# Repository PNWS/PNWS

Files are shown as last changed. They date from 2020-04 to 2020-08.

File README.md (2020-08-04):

## Do No Harm
Please ensure that if you are planning to deliver these to others that you sterilise them, always assume you are infected and take every precaution.

# PNWS
Face shield design to aid first line responders during the COVID19 Epidemic.   
This design was created by members of the Washington Sate 3D Face Shield Hub.  

If you are a medical professional and are in need of shields, please head to our website [faceshieldhub.org](https://www.faceshieldhub.org)

This is an update of "DtM-v3.1 Face Shield PPE, 3D printable headband NO LOGO", item 
3DPX-013359. 

# Available for Purchase
The PNWS is available for purchase at cost on amazon at the following link.  PLEASE MAKE SURE TO REMOVE THE PROTECTIVE FILM ON THE SHIELD BEFORE USE.
[https://www.amazon.com/dp/B08D7H37QX](https://www.amazon.com/dp/B08D7H37QX)

## Updates made based on clinical feedback are:
* Reduced mass and print time
* Improvements to shield retention while reducing stress applied to the shield itself.
* Thinned forehead section to reduce pressure on the forehead
* Mount peg spacing changed for equivalency to "Swedish" headband
* Added brimless variant to further reduce print time and mass
* Added engineering definition for face shield and headband
* Added cloth tie clips as an option
* Added option of foam headband
* Increased spacing to improve wearability with glasses and N95 mask underneath.
* Reduced weight solves for headaches from all-day wear of previous model

* Optimised build and assembly to standard materials that can be readily purchased (e.g., US letter-sized transparency)

## Product Point of View
Due to a domestic supply chain gap for transparent face shields, this remixed 3D printed design immediately provides personal protective equipment (PPE) to healthcare workers responding to COVID-19, and incorporates clinical feedback and clinical reviews from other similar designs being used across hospitals across the nation. Face shield characteristics: 
* limits aerosol and splatter exposure directly to the anterior head, specifically to the face and from above the head, while providing top ventilation to limit fogging and condensation
* reduces aerosol and splatter exposure on N95 and other face masks; this follows current recommendations to use full face shields to protect limited supply N95 masks
* re-usable for a single user (can survive multiple daily washes; transparent visor can be replaced from readily sourced materials when worn out)

easy to fabricate within a few days of design approval (i.e., no complex supply chains or production bottlenecks)
comfortable to wear and easy to don and doff (as it will be taken on and off dozens of times in a 12-24 hour shift)
provides protection to broader area of face compared to standard safety goggles or glasses

## LICENSING AND TERMS
License - Apache 2.

## Folder Structure
Once you download the fabrication package you will be see there is an assembly drawing and a BOM, please open these first to help decide which parts you would like to print.

## What to make?

### PNWS Frame:
Download the PNWS Full Release Package

NIH Link - https://3dprint.nih.gov/discover/3dpx-013883

### PNWS Short:
Download the PNWS Short Release Package

NIH Link - https://3dprint.nih.gov/discover/3dpx-013884

### Are any sliced files ready for my printer or ply cutter?

Yes! Please look at the [Sliced Files folder](https://github.com/mrjonny2/PNWS/tree/master/Sliced%20Files).  If you would like to contribute to these please reach out and we can get them added.

### What are the Cloth Ties?
If you can't get stretchy fabrics or button hole elastic use two cloth ties and any fabric or elastic to make a headband.

### How do I put it all together?
Please open: [PNWS Assembly Instructions.pdf](https://github.com/mrjonny2/PNWS/blob/master/PNWS%20Assembly%20Instructions.pdf)

## 3D PRINTING INFORMATION
__Please see the [Sliced Files folder](https://github.com/mrjonny2/PNWS/tree/master/Sliced%20Files) for files that are ready for cutting and printing__
### Printer technology/material
Intended Method - Fused Deposition Modeling

Acceptable Methods - Multi Jet Fusion, Selective Laser Sintering
### Printer Make/Model:
Intended: Testing and design carried out on Prusa Mk3 and Prusa Mk3S

Acceptable: Any printer using the technologies stated above
### Print Units:
mm (Detailed drawings for each part are provided)
### Scale at given print units:
1:1 scale
### Print Materials:
Preferred: PETG

Acceptable: ABS, PC, NYLON, PEEK, ULTEM, ASA or any other non-biodegradable polymer
### Number of prints per build build space:
Printer Dependant, 1 to multiple possible
### Print Time:
1h 3m using 0.6 nozzle, 0.4 layer height, pre-programmed settings.
### Pre- and post processing instructions:
Slicing required prior to printing specific to user's printer.   
#### Slice Recommendations for 0.4mm Nozzle
* Layer Height = 0.3mm
* First Layer height = 0.2mm
* Perimeters = 2
* Top solid layers = 3
* Bottom Solid Layers = 3
* Fill Density = 15%
* Fill pattern = Rectilinear
* No support Material
* No Raft    

This is generally identical to the Default PrusaSlicr 0.3mm Draft with the exception of reducing fill density to 15%.    

If you experience stringing on your prints, drop your nozzle temp for all but the first layer by 5C

Post-process as needed in accordance with provided drawings.

## Variants
There are a couple variations for this face shield, there is the shorty and the full variations which reduce mass while reducing the protection slightly.

The headband can also be swapped for the cloth tie clips and string or elasticated fabric

Shorty Variant:  
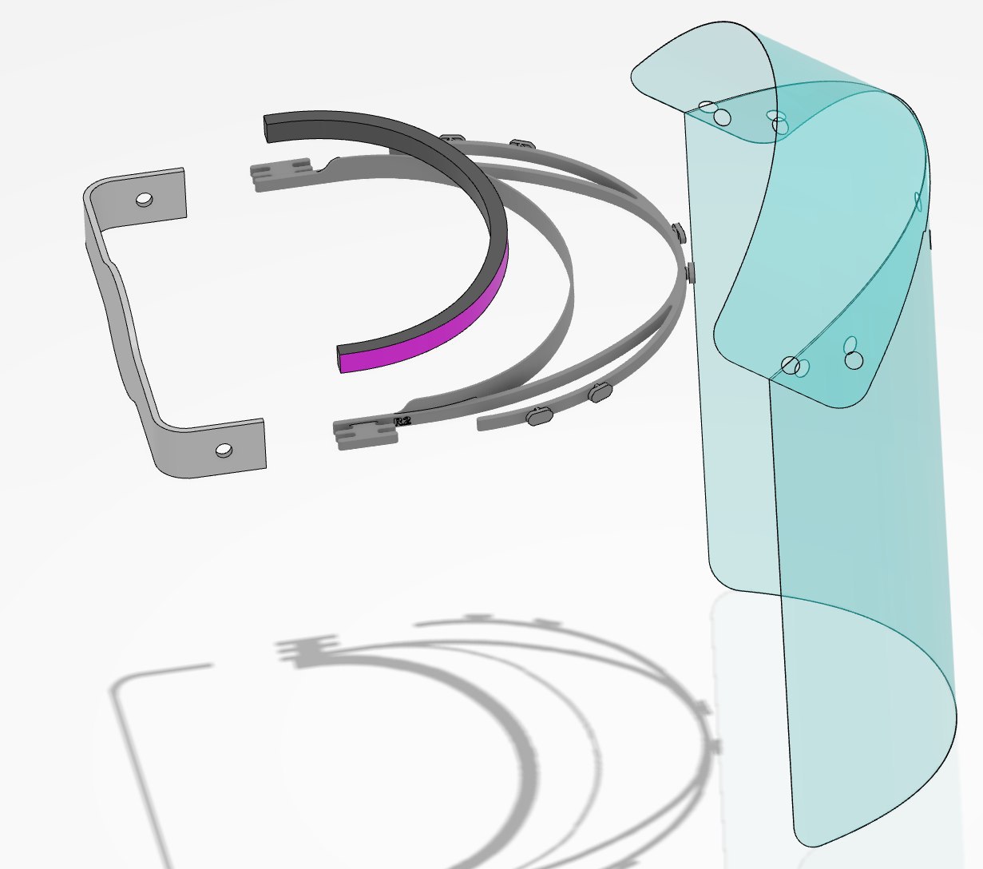
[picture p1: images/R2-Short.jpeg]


[Shorty]: https://raw.githubusercontent.com/mrjonny2/PNWS/master/images/R2-Short.jpeg "Shorty Variant"

Full Variant:  
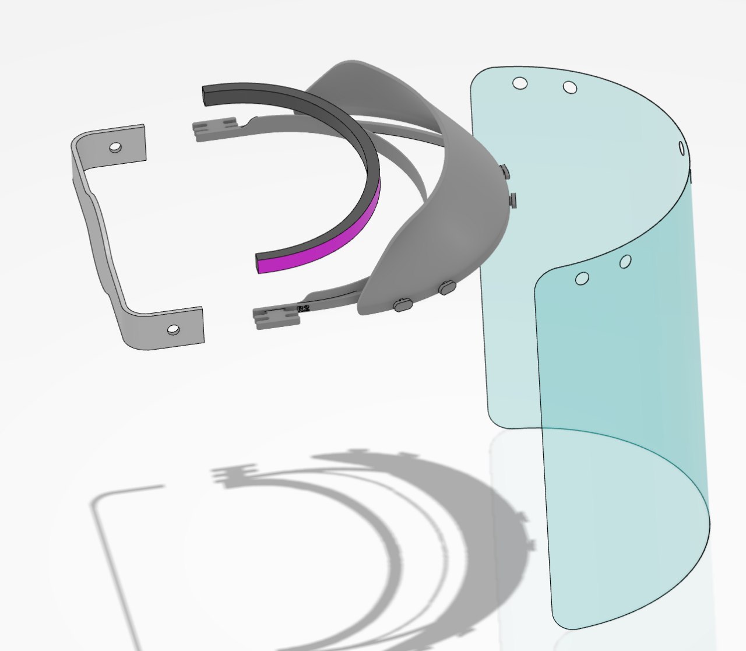
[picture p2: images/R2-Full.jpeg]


[Full]: https://raw.githubusercontent.com/mrjonny2/PNWS/master/images/R2-Full.jpeg "Full Variant"

## Shield Go-Gauge

If you are manufacturing shields, please print one of these go gauges to help verify that your hole punches are good.

## Contributors
Individuals directly contributing to this design include:

* Alice Ferng
* Inna Turevsky
* James Gwertzman
* Jason Vandervlugt
* Jonny Flowers
* Jon Friedman
* Mandi Mckay
* Neil Cueto
* Tom L
* Troy Hutt
* Yasuhiro Wabiko

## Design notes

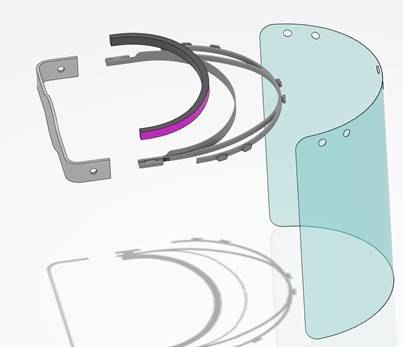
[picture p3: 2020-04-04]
images/R1-Short.jpg

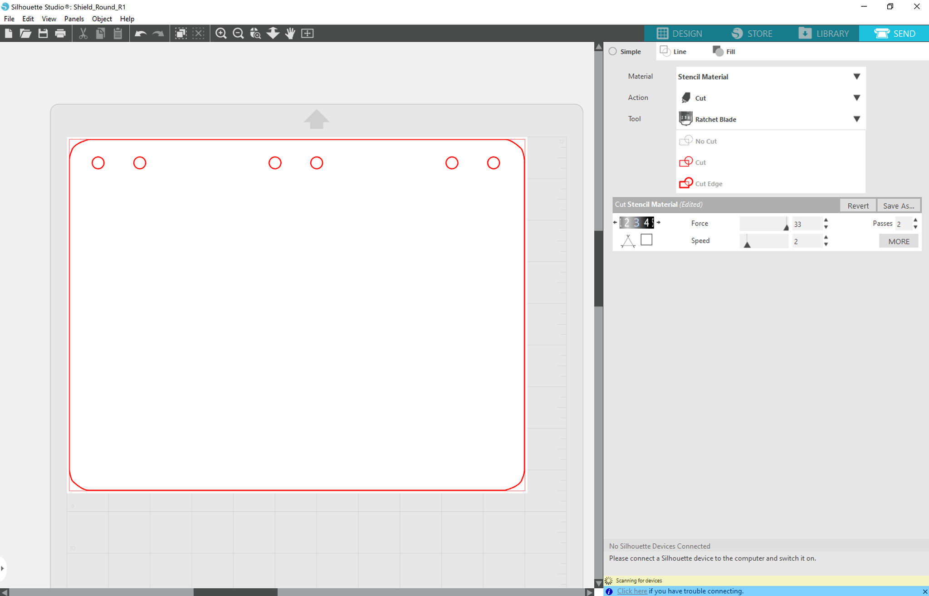
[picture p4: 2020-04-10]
Sliced Files/Silhouette Studio3/Studio3Screenshot.png

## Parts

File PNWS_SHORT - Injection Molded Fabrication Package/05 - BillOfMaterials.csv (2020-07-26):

Enovia Confidential Printed copies are Uncontrolled.
Generated on Jul 22
130879 rev 2: Engineering Bill of Materials
Level | Part Number | Revision | Specification Title | Qty | Type | Description
1 | 130879 | 2 | Asssmebly, Face Shield, PNWS | 1 | Assembly | Faceshield Released in response to the COVID19 epidemic released under MIT license
2 | 130007 | 3 | Headband Elastic | 1 | Part | Button hole elastic
2 | 128836 | 2 | Foam for Frame | 1 | Part | Neoprene Foam
2 | 130887 | 2 | Shield, Origami | 1 | Part | Polycarbonate shield
2 | 129016 | 2 | Frame, Short, PNWS, Injection Molding | 1 | Part | PET Injection molded frame

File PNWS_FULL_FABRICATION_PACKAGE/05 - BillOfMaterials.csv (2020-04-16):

Enovia Confidential Printed copies are Uncontrolled.
Generated on Apr 15
128827 rev 3: Engineering Bill of Materials
Level | Strap Variant | Revision | Specification Title | Qty | Type | Description
1 |  | 2 | ASSY, FACESHIELD, PNWS | 1 | Assembly | Faceshield Released in response to the COVID19 epidemic released under MIT license
2 | -- | 2 | FACESHIELD, FRAME, PNWS | 1 | Part
2 | -- | 1 | FACESHIELD, PNWS R1 | 1 | Part
2 | Headband | 1 | HEADBAND, FACESHIELD, PNWS | 1 | Part
2 | -- | 2 | FACESHIELD, FRAME, SHORT, PNWS | 1 | Part
2 | Cloth Tie | 1 | FACESHIELD, CLOTH TIE | 2 | Part | Optional for use with generic fabrics to tie mask
2 | -- | 1 | FACESHIELD, FOAM | 1 | Part

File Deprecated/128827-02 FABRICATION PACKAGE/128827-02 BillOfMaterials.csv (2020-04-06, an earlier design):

Enovia Confidential Printed copies are Uncontrolled.
Generated on Apr 6 |  |  | 2020 3:31:45 AM
128827 rev 2: Engineering Bill of Materials
Level | Shield Variant | Strap Variant | Part Number | Revision | Specification Title | Qty | Type | Description
1 |  |  | 128827 | 2 | ASSY, FACESHIELD, PNWS | 1 | Assembly | Faceshield Released in response to the COVID19 epidemic released under MIT license
2 | Brimmed | -- | 128828 | 2 | FACESHIELD, FRAME, PNWS | 1 | Part
2 | Brimmed | -- | 128829 | 1 | FACESHIELD, PNWS R1 | 1 | Part
2 | Both | Headband | 128830 | 1 | HEADBAND, FACESHIELD, PNWS | 1 | Part
2 | Short | -- | 128831 | 2 | FACESHIELD, FRAME, SHORT, PNWS | 1 | Part
2 | Both | Cloth Tie | 128835 | 1 | FACESHIELD, CLOTH TIE | 2 | Part | Optional for use with generic fabrics to tie mask
2 | Both | -- | 128836 | 1 | FACESHIELD, FOAM | 1 | Part
2 | Short | -- | 128839 | 1 | FACESHIELD, ORIGAMI, PNWS | 1 | Part

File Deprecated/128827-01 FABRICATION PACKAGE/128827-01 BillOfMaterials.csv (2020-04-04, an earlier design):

Enovia Confidential Printed copies are Uncontrolled.
Generated on Apr 4 |  |  | 2020 9:04:41 PM
128827 rev 1: Engineering Bill of Materials
Level | Shield Variant | Strap Variant | Part Number | Revision | Specification Title | State | Qty | Type | Description
1 |  |  | 128827 | 1 | ASSY, FACESHIELD, PNWS | Released | 1 | Assembly | Faceshield Released in response to the COVID19 epidemic released under MIT license
2 | Both | Both | 128829 | 1 | FACESHIELD, PNWS R1 | Released | 1 | Part
2 | Full | Both | 128828 | 1 | FACESHIELD, FRAME, PNWS | Released | 1 | Part
2 | Both | Band | 128830 | 1 | HEADBAND, FACESHIELD, PNWS | Released | 1 | Part
2 | Short | Both | 128831 | 1 | FACESHIELD, FRAME, SHORT, PNWS | Released | 1 | Part
2 | Both | Clothtie | 128835 | 1 | FACESHIELD, CLOTH TIE | Released | 2 | Part | Optional for use with generic fabrics to tie mask
2 | Both | Both | 128836 | 1 | FACESHIELD, FOAM | Released | 1 | Part

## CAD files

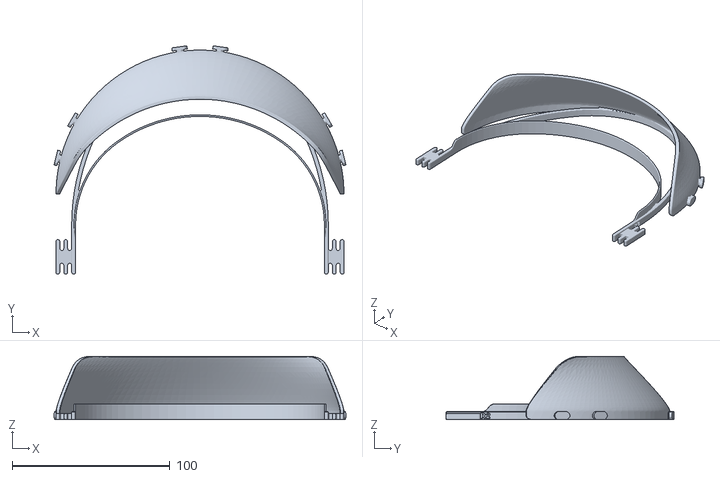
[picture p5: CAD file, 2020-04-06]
PNWS_FULL_FABRICATION_PACKAGE/06 - Frame - Full/06b - Frame - Full - STL.stl
185.0 x 144.7 x 40.0

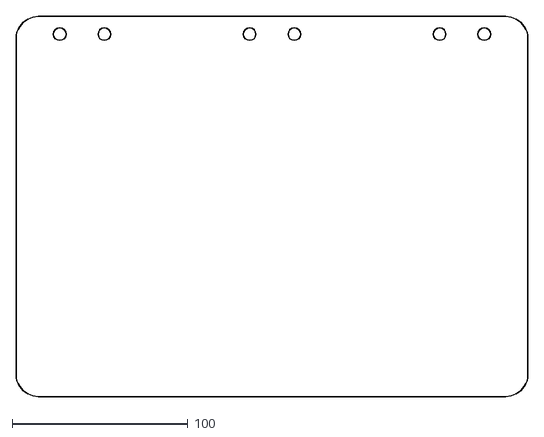
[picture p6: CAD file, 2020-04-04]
PNWS_FULL_FABRICATION_PACKAGE/07 - Shield/07c - Shield - DXF.dxf
290.9 x 216.0

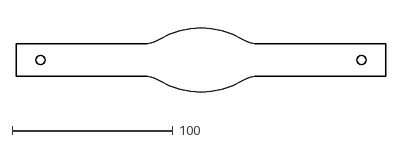
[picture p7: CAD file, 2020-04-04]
PNWS_FULL_FABRICATION_PACKAGE/08 - Headband - Elastic/08b - Headband - Elastic - DXF.dxf
229.8 x 44.8

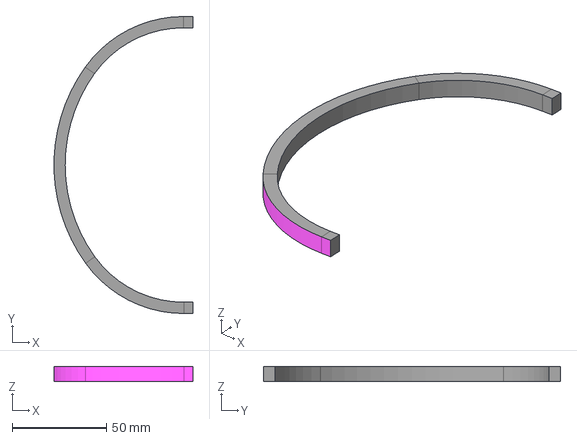
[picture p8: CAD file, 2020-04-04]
PNWS_FULL_FABRICATION_PACKAGE/09 - Foam - For Frame (Optional)/09c - Foam - For Frame - STP.stp
73.7 x 157.6 x 8.00 mm

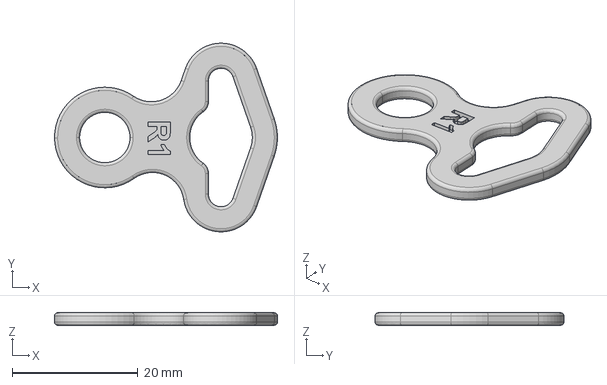
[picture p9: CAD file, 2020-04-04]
PNWS_FULL_FABRICATION_PACKAGE/10 - Cloth Tie (Optional)/10d - Cloth Tie - IGS.igs
35.4 x 30.0 x 2.00 mm

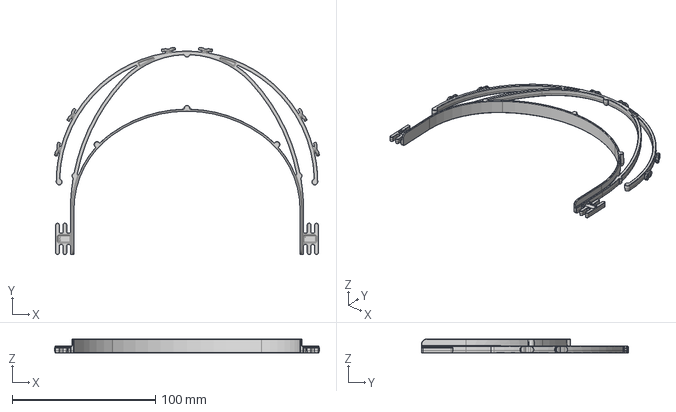
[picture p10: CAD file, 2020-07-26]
PNWS_SHORT - Injection Molded Fabrication Package/06 - Frame - Short - Injection Molding/06b - Frame - Short - Injection Molding - STEP.stp
184.8 x 144.6 x 10.0 mm

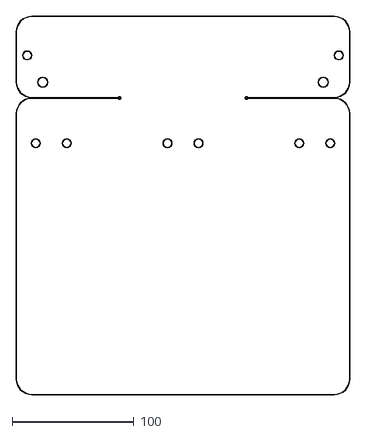
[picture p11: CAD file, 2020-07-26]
PNWS_SHORT - Injection Molded Fabrication Package/07 - Shield - Origami/07c - Shield - Origami - DXF.dxf
273.0 x 310.0

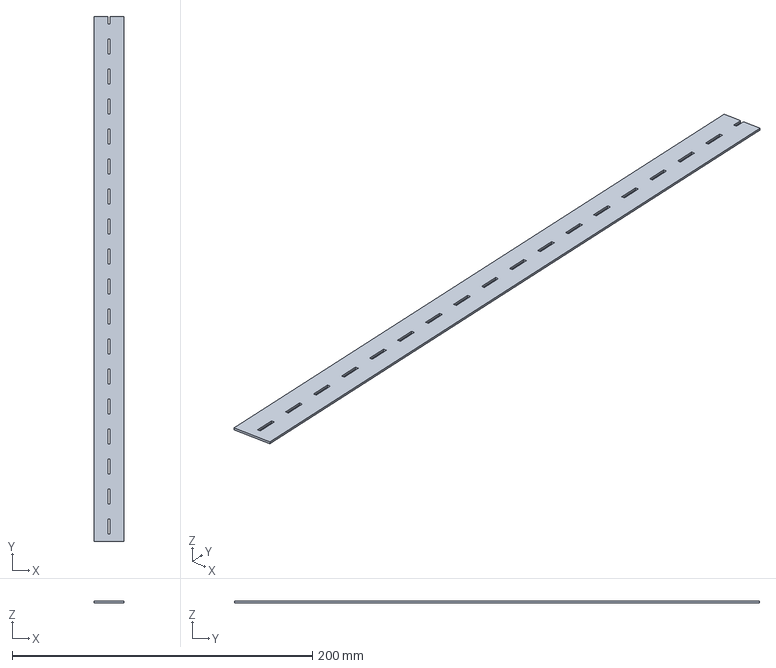
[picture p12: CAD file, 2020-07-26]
PNWS_SHORT - Injection Molded Fabrication Package/08 - Headband - Elastic/08c - Headband - Elastic - 3D IGS.igs
20.0 x 350.0 x 1.00 mm

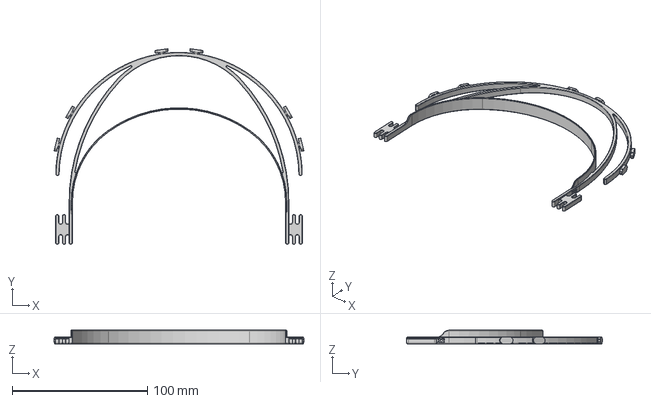
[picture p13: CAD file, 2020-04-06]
PNWS_SHORT_FABRICATION_PACKAGE/06 - Frame - Short/06d - Frame - Short - IGS.igs
185.0 x 144.7 x 10.0 mm

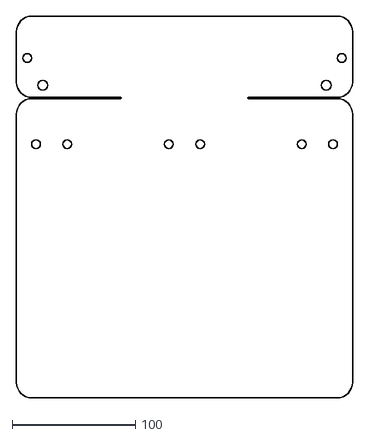
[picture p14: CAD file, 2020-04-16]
PNWS_SHORT_FABRICATION_PACKAGE/07 - Shield - Origami/07c - Shield - Origami - DXF.dxf
273.0 x 310.0

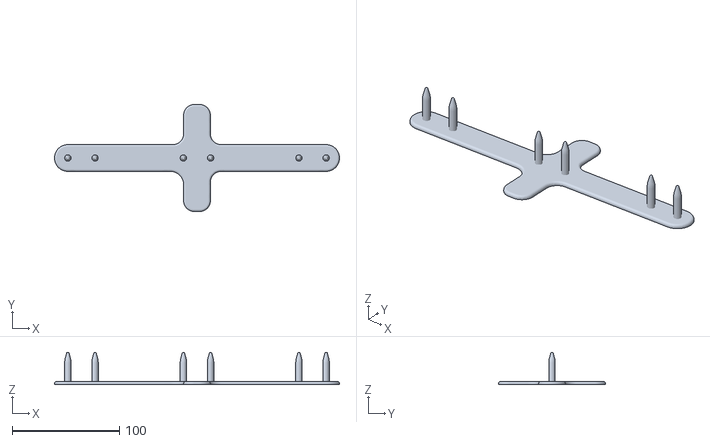
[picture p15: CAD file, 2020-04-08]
SHIELD GO GAUGE.stl
266.3 x 100.0 x 30.0

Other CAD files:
PNWS_FULL_FABRICATION_PACKAGE/06 - Frame - Full/06d - Frame - Full - IGS.igs
PNWS_FULL_FABRICATION_PACKAGE/06 - Frame - Full/06c - Frame - Full - STP.stp
PNWS_SHORT - Injection Molded Fabrication Package/09 - Foam - For Frame/09c - Foam for Frame - 3D IGS.igs
PNWS_SHORT_FABRICATION_PACKAGE/11 - Frame - Short - Injection Molding/11b - Frame - Short - Injection Molding - STP.stp
Deprecated/128827-01 FABRICATION PACKAGE/128828 FACESHIELD FRAME PNWS/128828-01 FACESHIELD FRAME PNWS A.1 Released.igs
Deprecated/128827-01 FABRICATION PACKAGE/128828 FACESHIELD FRAME PNWS/128828-01 FACESHIELD FRAME PNWS A.1 Released.stp
Deprecated/128827-01 FABRICATION PACKAGE/128829 FACESHIELD PNWS R1/128829-01 FACESHIELD PNWS R1 A.1 Released.igs
Deprecated/128827-01 FABRICATION PACKAGE/128829 FACESHIELD PNWS R1/128829-01 FACESHIELD PNWS R1 A.1 Released.stp
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

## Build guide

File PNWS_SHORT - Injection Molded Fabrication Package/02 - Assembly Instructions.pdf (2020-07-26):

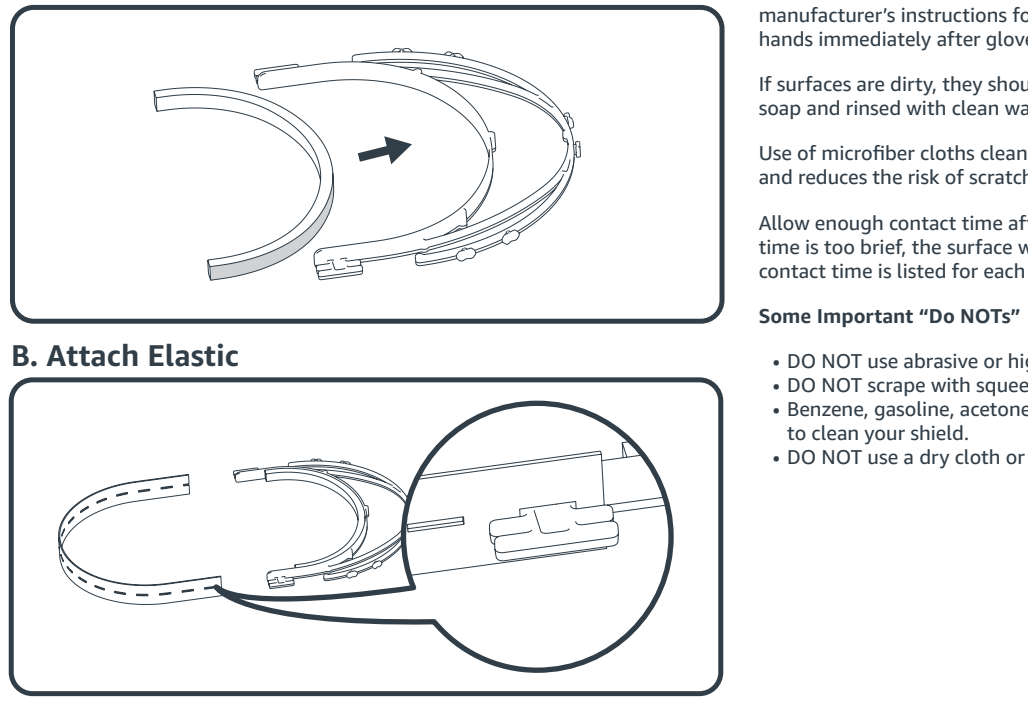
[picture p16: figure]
B. Attach Elastic; Some Important “Do NOTs”; to clean your shield.

## CLEANING METHODS

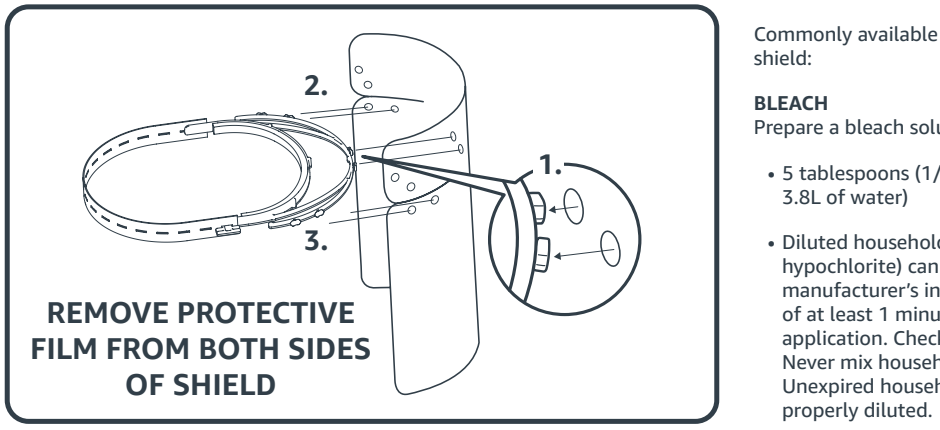
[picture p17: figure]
shield:; BLEACH; 3.8L of water); properly diluted.; REMOVE PROTECTIVE FILM FROM BOTH SIDES OF SHIELD

Commonly available disinfectants are recommended to be used on your face

Prepare a bleach solution by mixing:

- 5 tablespoons (1/3rd cup) bleach per gallon of water (80mL bleach per
- Diluted household bleach solutions (at least 1000ppm sodium hypochlorite) can be used if appropriate for the surface. Follow manufacturer’s instructions for application, ensuring a contact time of at least 1 minute, and allowing proper ventilation during and after application. Check to ensure the product is not past its expiration date. Never mix household bleach with ammonia or any other cleanser. Unexpired household bleach will be effective against coronaviruses when

SUPER SANI-WIPE, ISOPROPYL ALCOHOL [IPA] or ETHYL ALCOHOL
Use of alcohol-based wipes or sprays or soaked cloths containing at least 70%

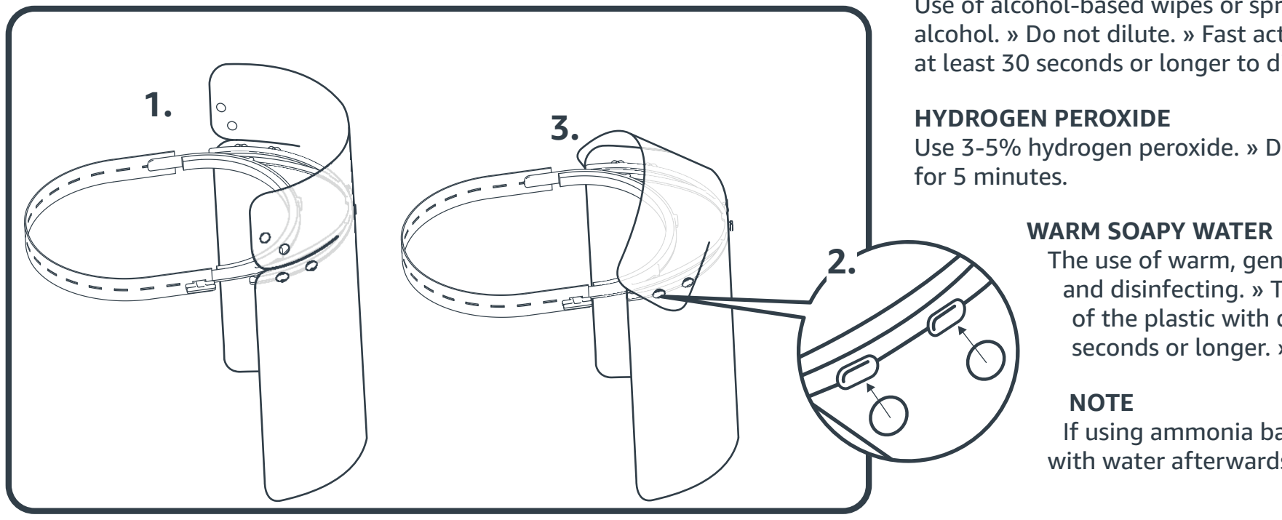
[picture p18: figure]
HYDROGEN PEROXIDE; for 5 minutes.; WARM SOAPY WATER; NOTE

alcohol. » Do not dilute. » Fast acting. Allow alcohol to remain on surface for at least 30 seconds or longer to disinfect.

Use 3-5% hydrogen peroxide. » Do not dilute. » Allow to remain on the plastic

The use of warm, gentle dish soap is a common form of cleaning and disinfecting. » Thoroughly and vigorously wash the surface of the plastic with dish washing soap for a minimum of 20 seconds or longer. » Rinse with clean water

If using ammonia based cleaners rinse down the clear shield with water afterwards to preserve optical clarity.

## A. Attach Foam

## C. Snap on Shield

## D. Fold Shield

## CLEANING INSTRUCTIONS

Wear disposable gloves when cleaning and disinfecting surfaces. Gloves should be discarded after each cleaning. If reusable gloves are used, those gloves should be dedicated for cleaning and disinfection of surfaces
for COVID-19 and should not be used for other purposes. Consult the manufacturer’s instructions for cleaning and disinfection products used. Clean hands immediately after gloves are removed.

If surfaces are dirty, they should be cleaned using a gentle warm dish washing soap and rinsed with clean water prior to disinfection.

Use of microfiber cloths cleans 50% better than comparable cotton towels and reduces the risk of scratching plastic.

Allow enough contact time after applying the disinfectant. If the contact time is too brief, the surface will not be thoroughly disinfected. Appropriate contact time is listed for each disinfectant listed below.

- DO NOT use abrasive or highly alkaline cleaners
- DO NOT scrape with squeegees, razor blades or other sharp instruments.
- Benzene, gasoline, acetone, or carbon tetrachloride should never be used
- DO NOT use a dry cloth or your hand to clean your polycarbonate!
Assembly Instructions - Open Source.indd 1 | 7/25/2020 10:09:41 PM

The Items are not intended for antimicrobial or antiviral protection or related uses, or uses for infection prevention or reduction or related uses, or for radiation protection, or any use that would create an undue risk in light of the public health emergency.

Copyright 2020 faceshieldhub.org

Licensed under the Apache License, Version 2.0 (the “License”); you may not use this file except in compliance with the License. You may obtain a copy of the License at:

http://www.apache.org/licenses/LICENSE-2.0

Unless required by applicable law or agreed to in writing, software distributed under the License is distributed on an “AS IS” BASIS, WITHOUT WARRANTIES OR CONDITIONS OF ANY KIND, either express or implied. See the License for the specific language governing permissions and limitations under the License.

These face shields are provided in parts meant to be assembled by the user.

The Items in this kit are not sterile.

Cleaning Methods are included with the Items in this package. Follow all cleaning agent manufacturer recommendations.

Assembly Instructions are included with the items in this package.

Alert: The design and materials for these face shields (“Items”) have been “Reviewed for Clinical Use” and made available by NIH/NIAD in collaboration with the U.S. Food and Drug Administration, the Veterans Healthcare Administration, and America Makes under on the NIH 3D Print Exchange (https://3dprint.nih.gov/collections/covid-19-response) including the following statements:

This design has undergone review in a clinical setting and has been found appropriate when fabricated with the printer type and materials specified.

https://3dprint.nih.gov/discover/3dpx-013884

March 25, 2020: [The NIH 3D Print Exchange] collection of designs was created to support the manufacturing of personal protective equipment (PPE) or other necessary medical devices that are in short supply due to the COVID-19 outbreak. While many can be printed with a 3D printer at home or your local Maker space, the NIH, FDA, VA, America Makes, and the contributing creators cannot ensure the quality, safety, and efficacy of these designs when manufactured without proper quality controls and processes.

We are proud to support you, and we thank you for all you are doing for our communities. We are grateful for your efforts.

NON
STERILE

This face shield was designed by an open source group of volunteers, source files and attributions can be found here:

github.com/PNWS/PNWS

For further information on products available for disinfecting your face shield, please visit:

https://www.epa.gov/pesticide-registration/list-n-disinfectants-use-against-sars-cov-2-covid-19

The Items contain materials which will contact the human body, including:

- Polyethylene Terephthalate Glycol (PETG) for the frame
- Polycarbonate (PC) for the shield
- Neoprene or Vinyl for the closed cell foam
- Cotton, Polyester, and Elastic for the headband, which may contain Latex

The Items are not intended for use in the presence of a high intensity heat sources or flammable gas. These Items should not be shared between users.

Document Version 2

Assembly Instructions - Open Source.indd 2 | 7/25/2020 10:09:41 PM

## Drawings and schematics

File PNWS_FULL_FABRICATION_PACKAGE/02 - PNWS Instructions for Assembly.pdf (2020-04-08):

# PNWS

# FACE SHIELD ASSEMBLY

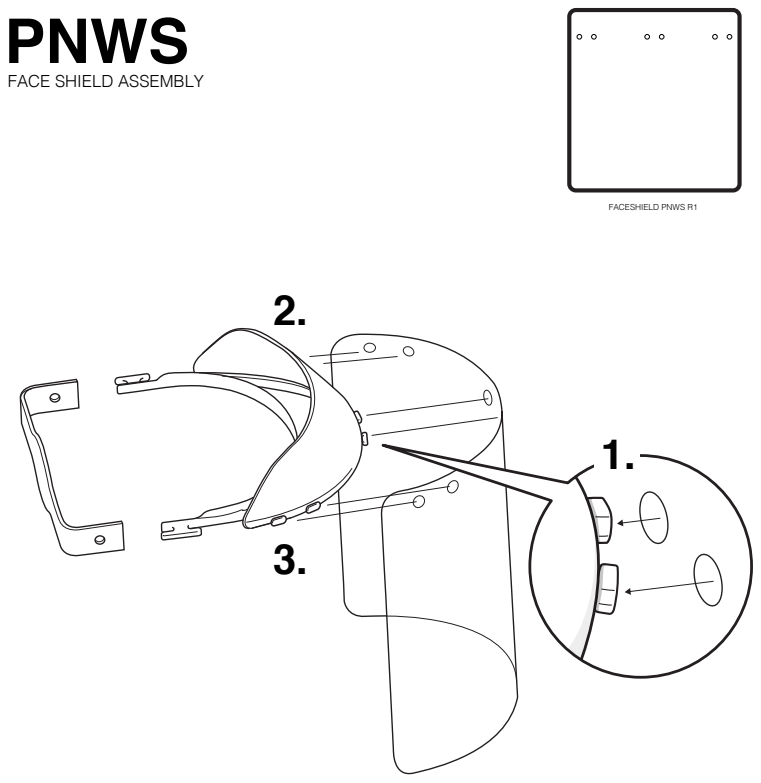
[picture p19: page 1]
FACESHIELD PNWS R1

# PNWS-SHORT

# FACE SHIELD ASSEMBLY

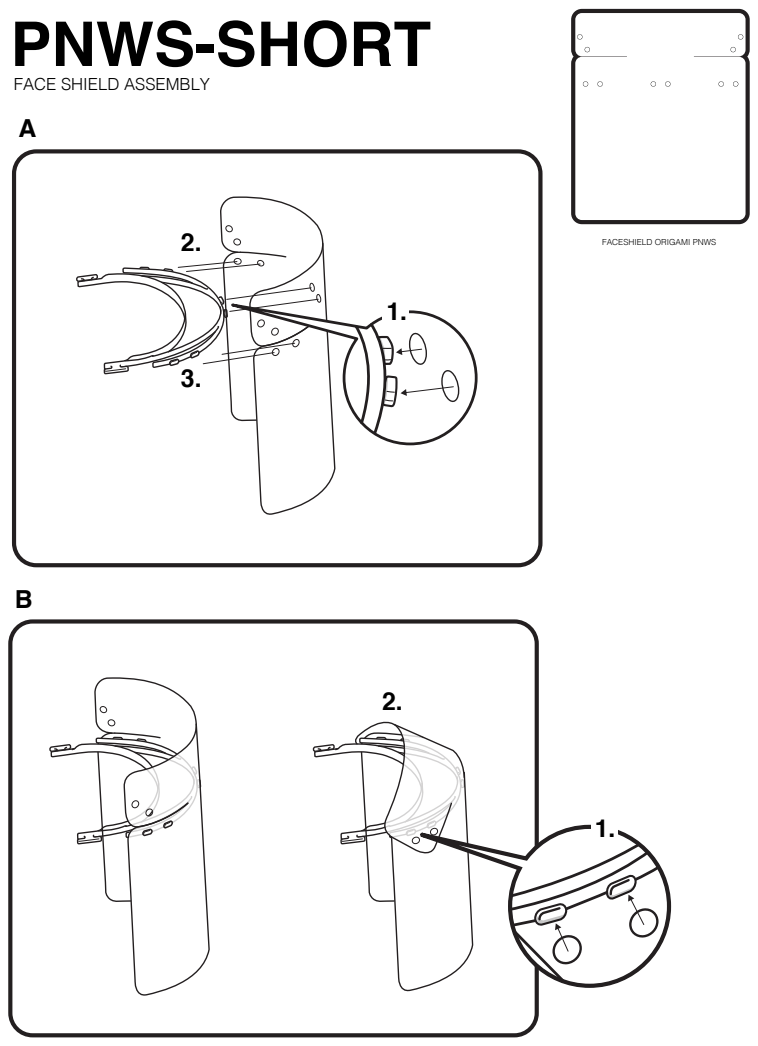
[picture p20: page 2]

2. FACESHIELD ORIGAMI PNWS

# PNWS

# HEADBAND ASSEMBLY

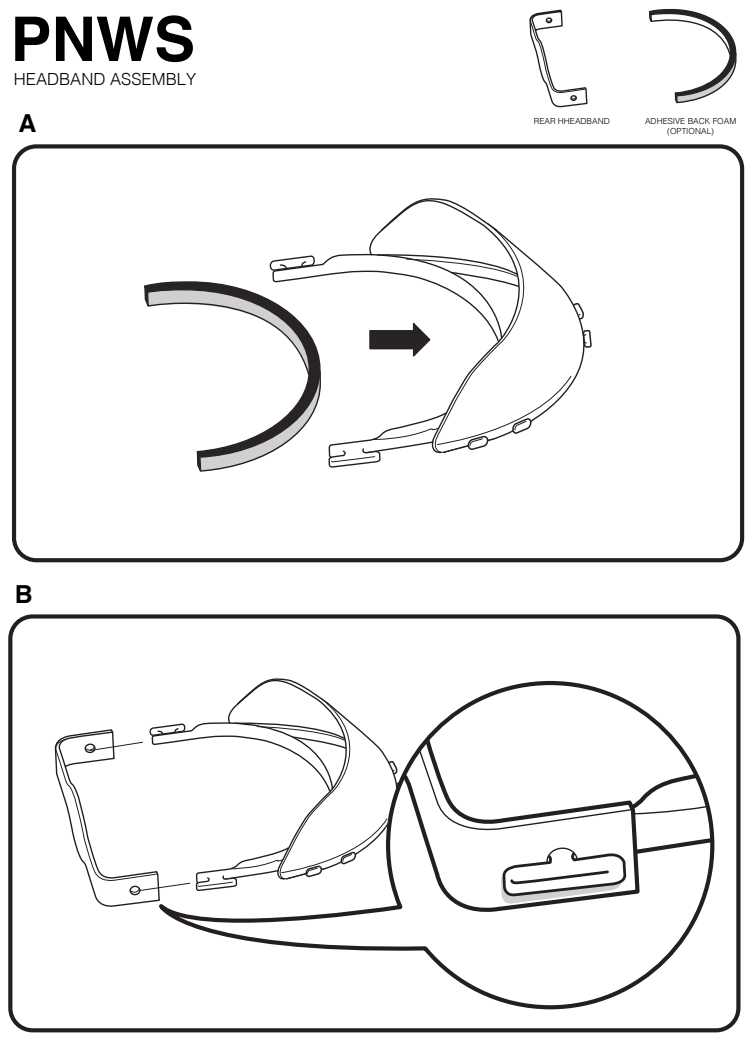
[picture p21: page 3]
(OPTIONAL) A; REAR HHEADBAND

ADHESIVE BACK FOAM

# PNWS

# HEADBAND ASSEMBLY

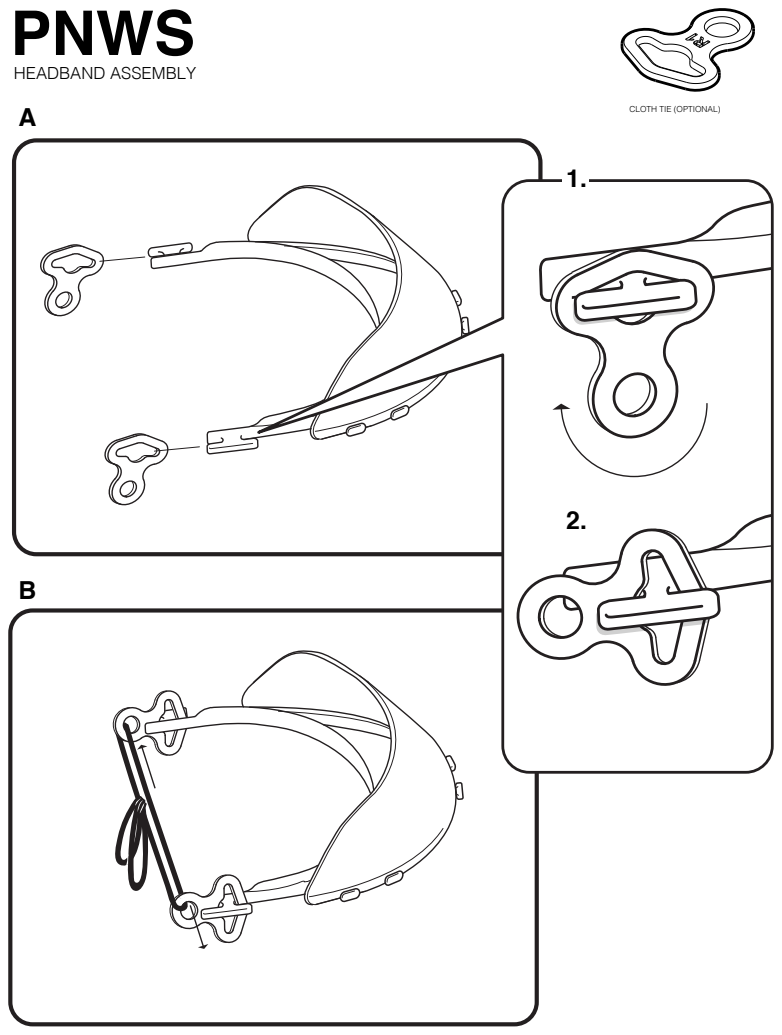
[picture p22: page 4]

CLOTH TIE (OPTIONAL) A

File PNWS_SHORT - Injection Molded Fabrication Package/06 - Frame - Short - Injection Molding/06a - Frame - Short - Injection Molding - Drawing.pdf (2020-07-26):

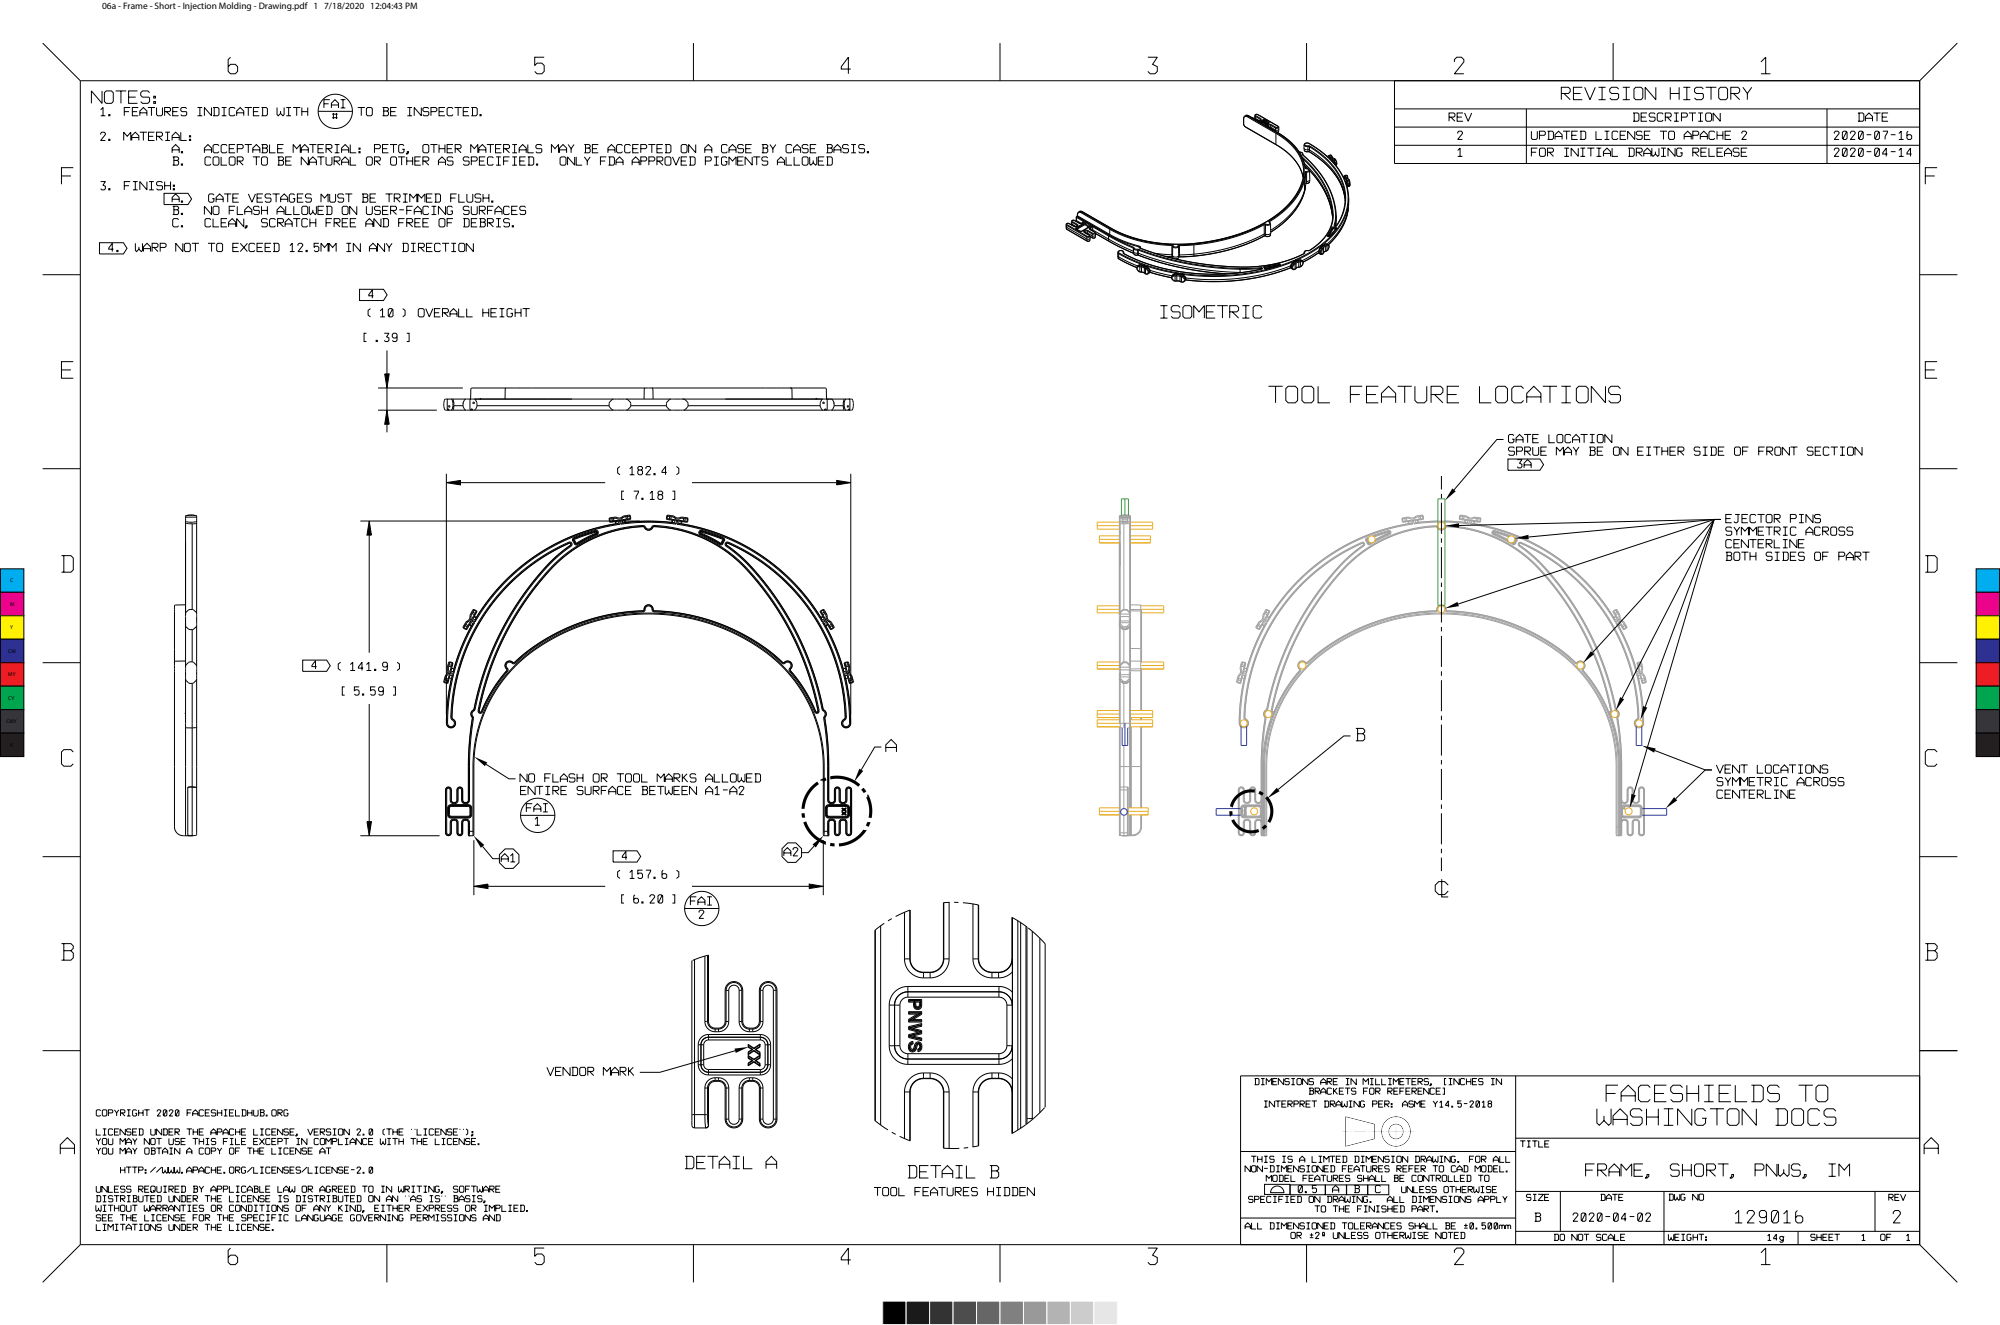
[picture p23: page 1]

06a - Frame - Short - Injection Molding - Drawing.pdf 1 7/18/2020 12:04:43 PM

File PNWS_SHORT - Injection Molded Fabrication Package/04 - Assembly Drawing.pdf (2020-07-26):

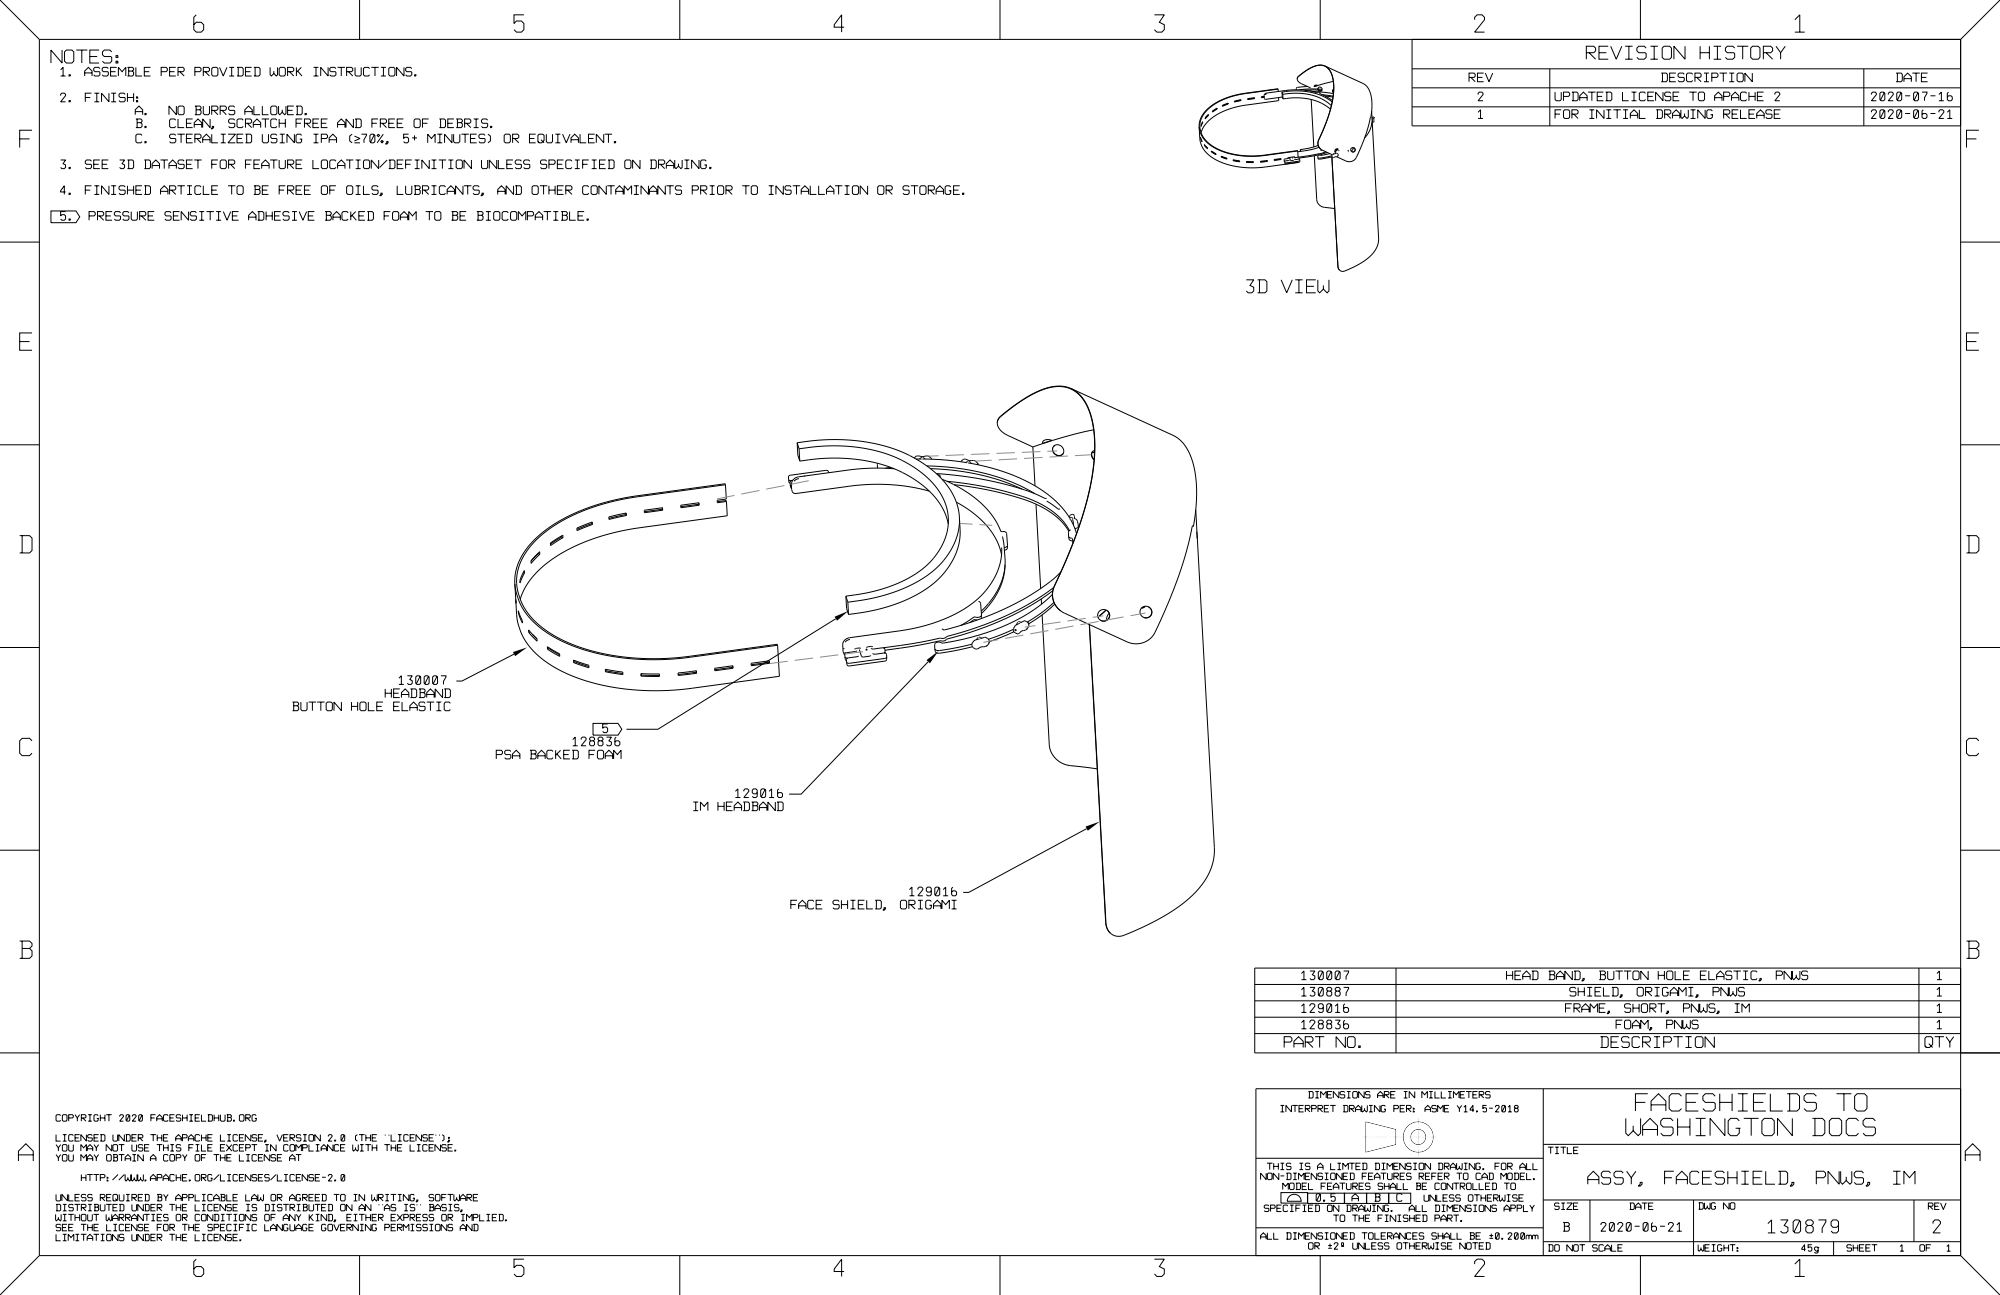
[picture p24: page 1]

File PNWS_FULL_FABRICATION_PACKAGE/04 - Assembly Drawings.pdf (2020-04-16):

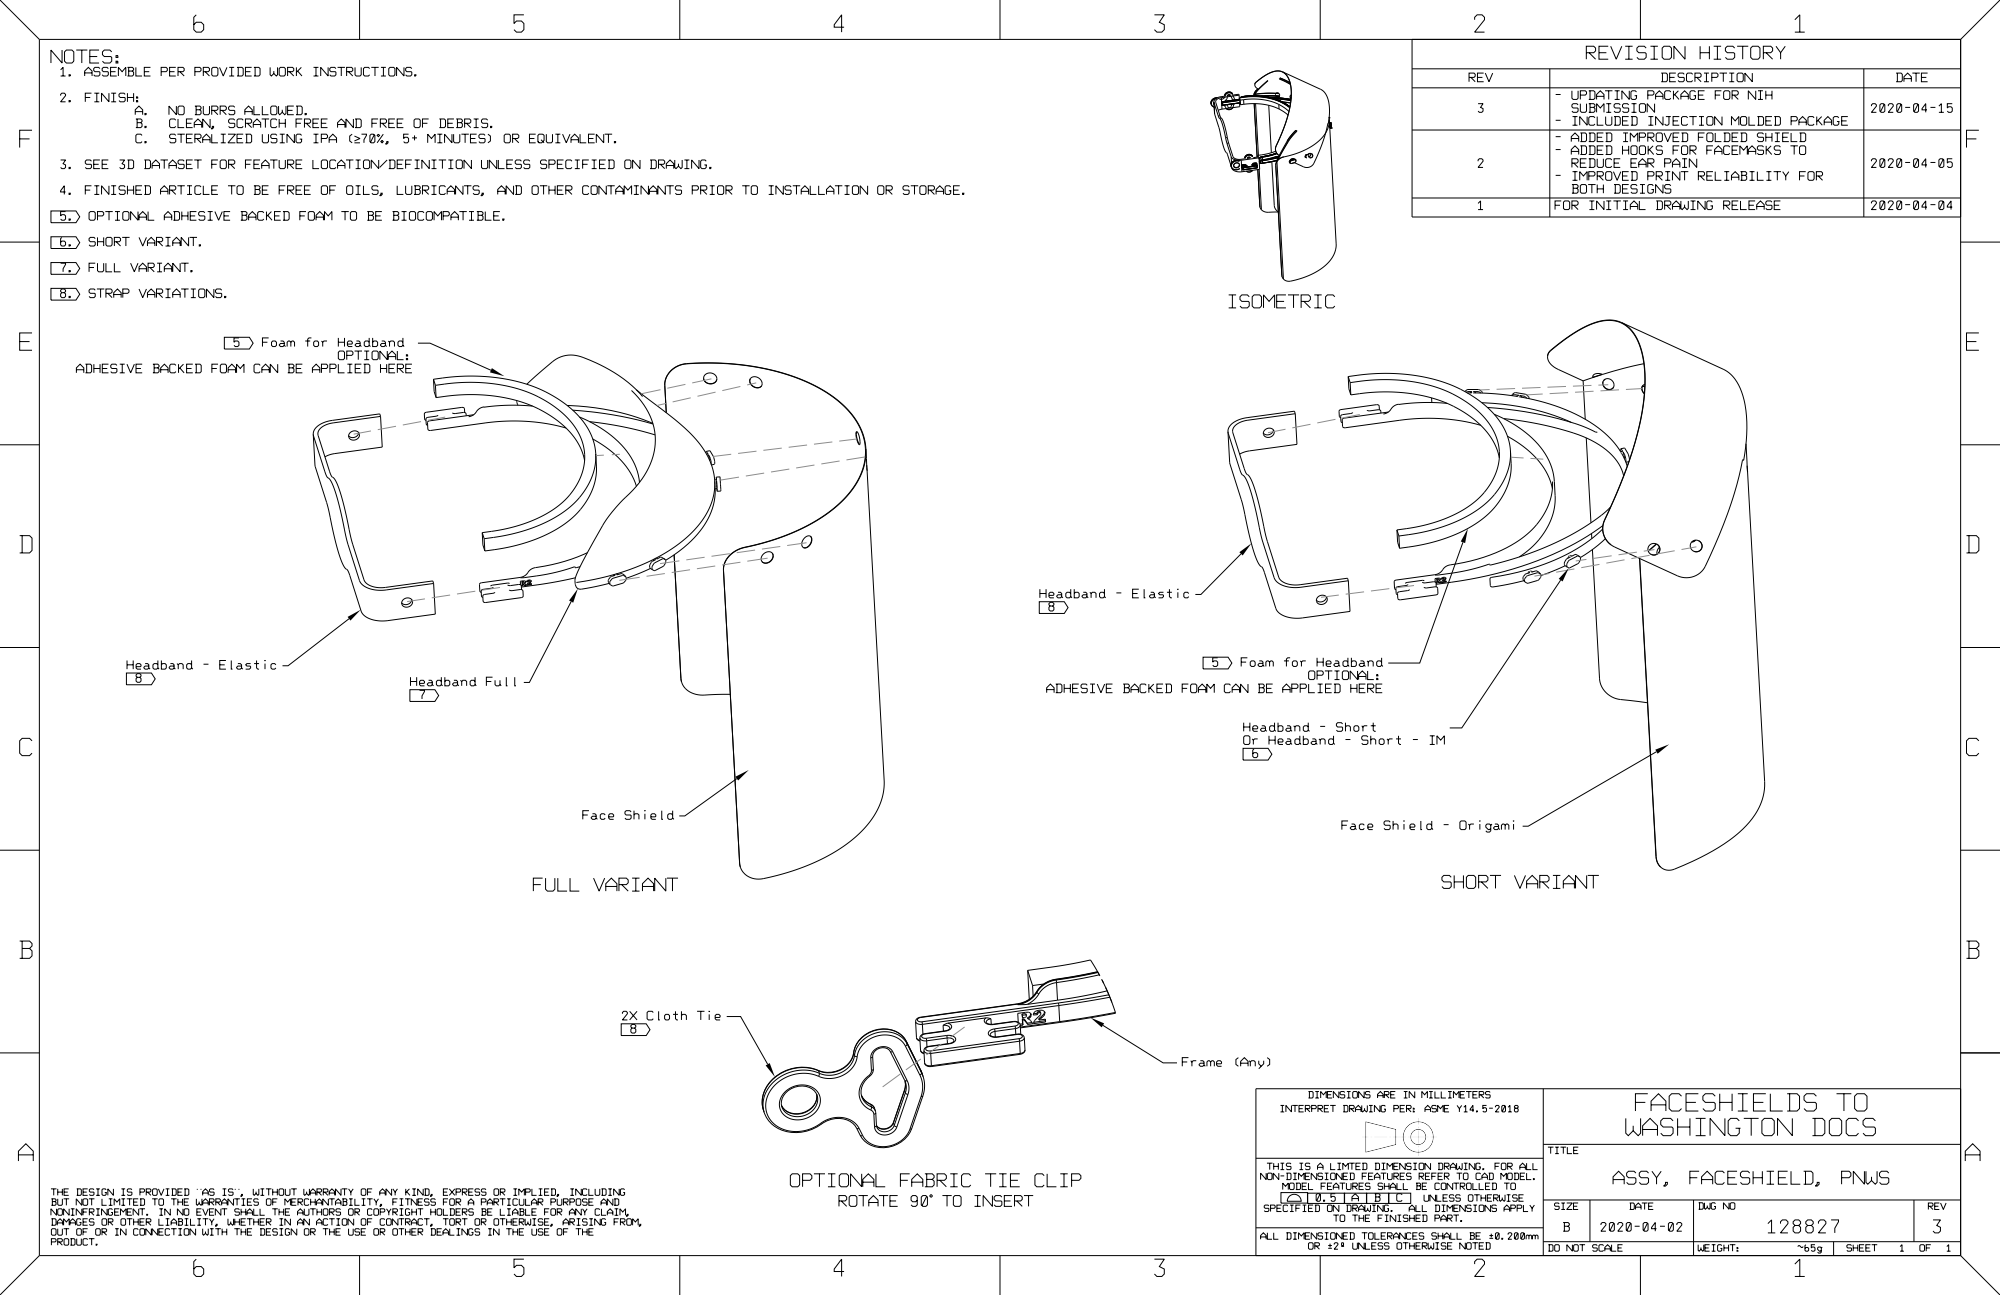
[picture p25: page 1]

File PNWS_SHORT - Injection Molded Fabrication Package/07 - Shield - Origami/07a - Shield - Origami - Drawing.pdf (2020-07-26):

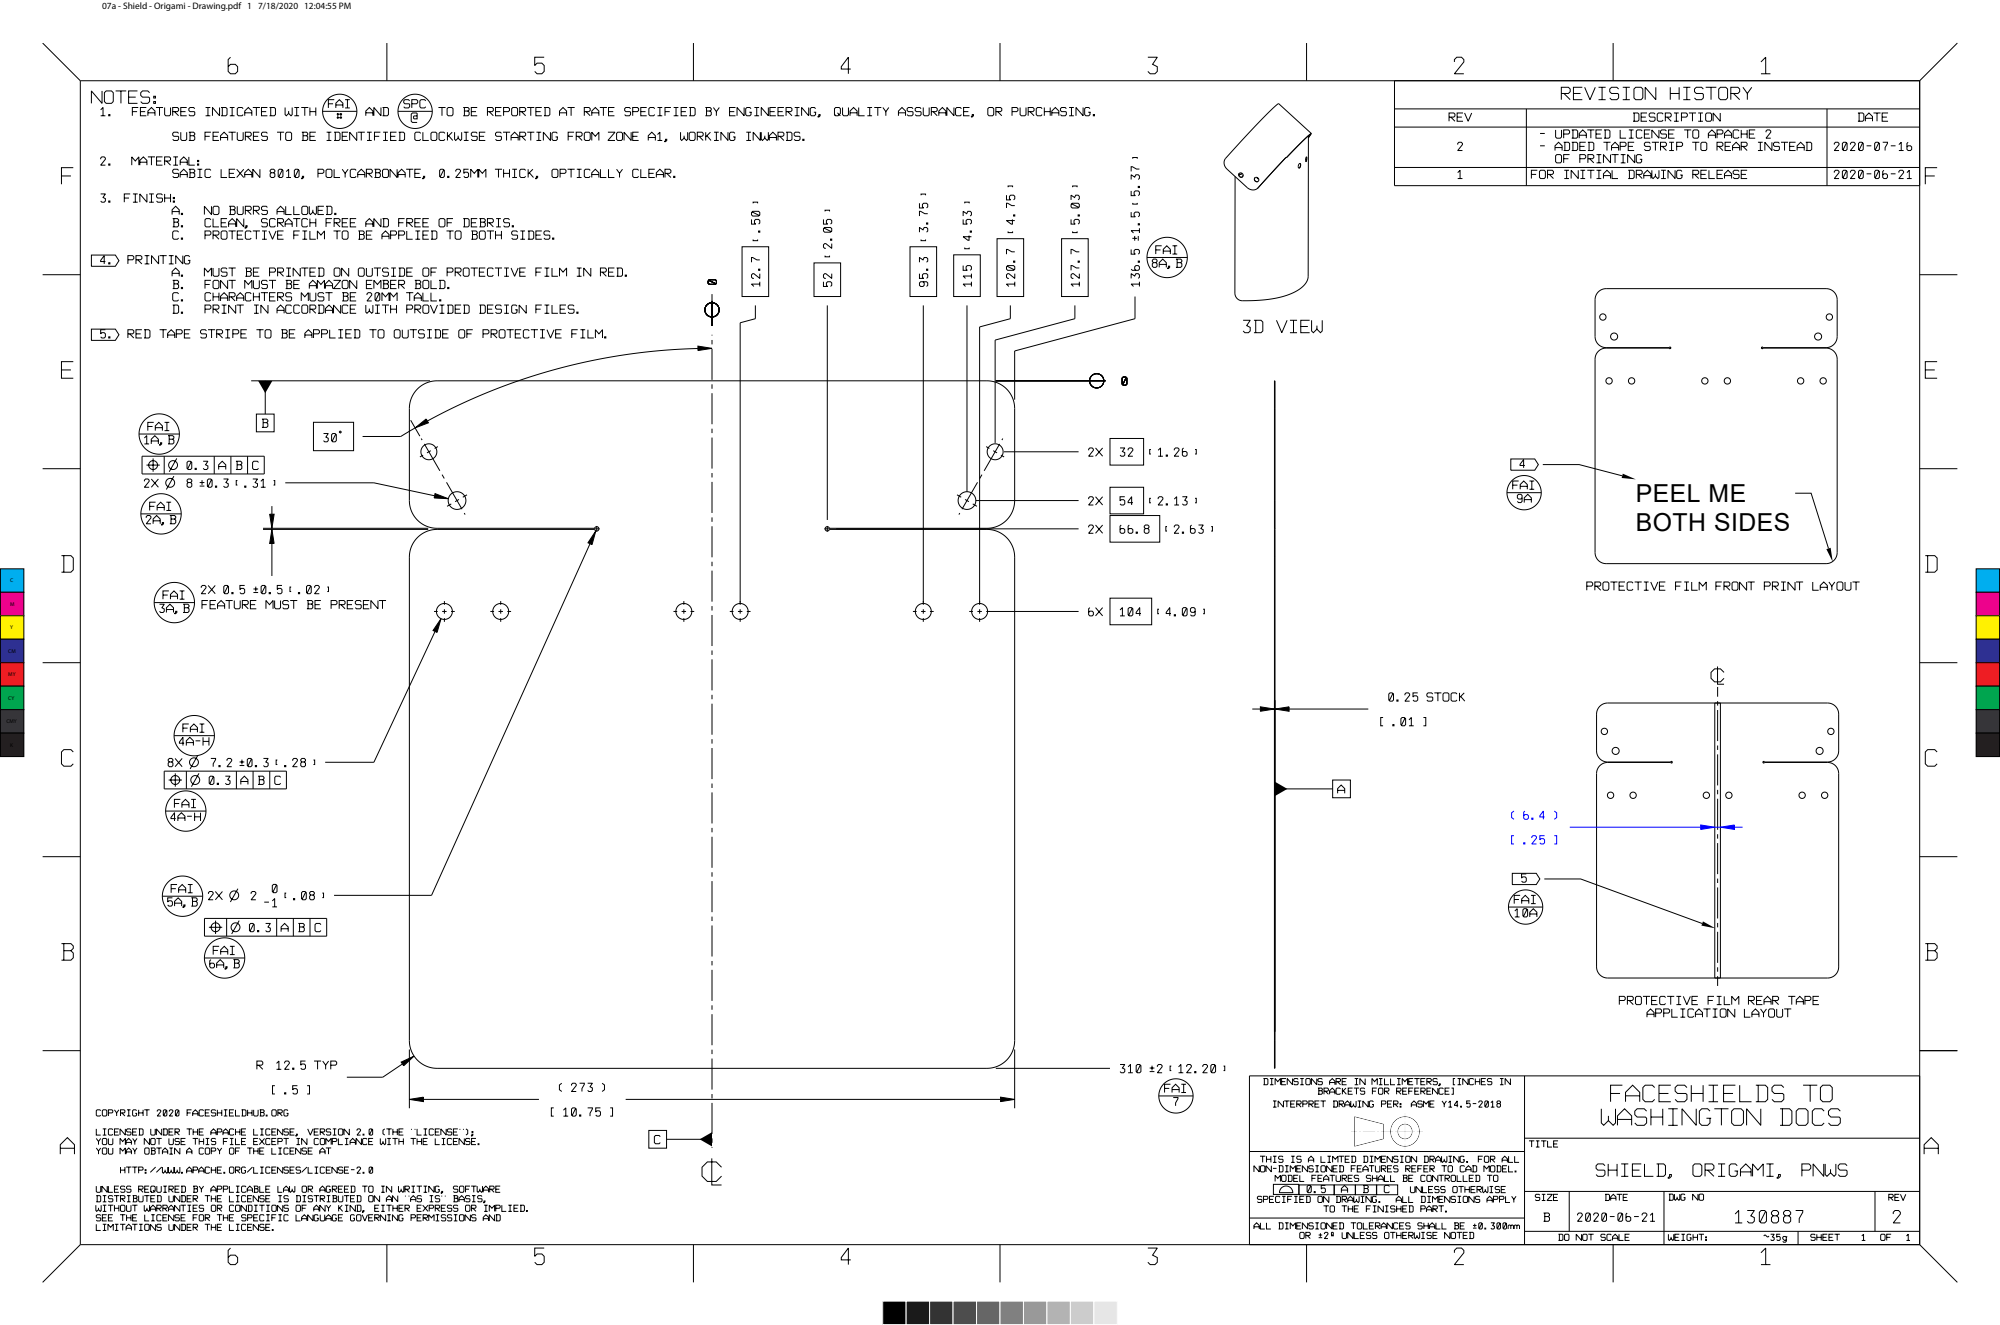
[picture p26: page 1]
PEEL ME BOTH SIDES

07a - Shield - Origami - Drawing.pdf 1 7/18/2020 12:04:55 PM

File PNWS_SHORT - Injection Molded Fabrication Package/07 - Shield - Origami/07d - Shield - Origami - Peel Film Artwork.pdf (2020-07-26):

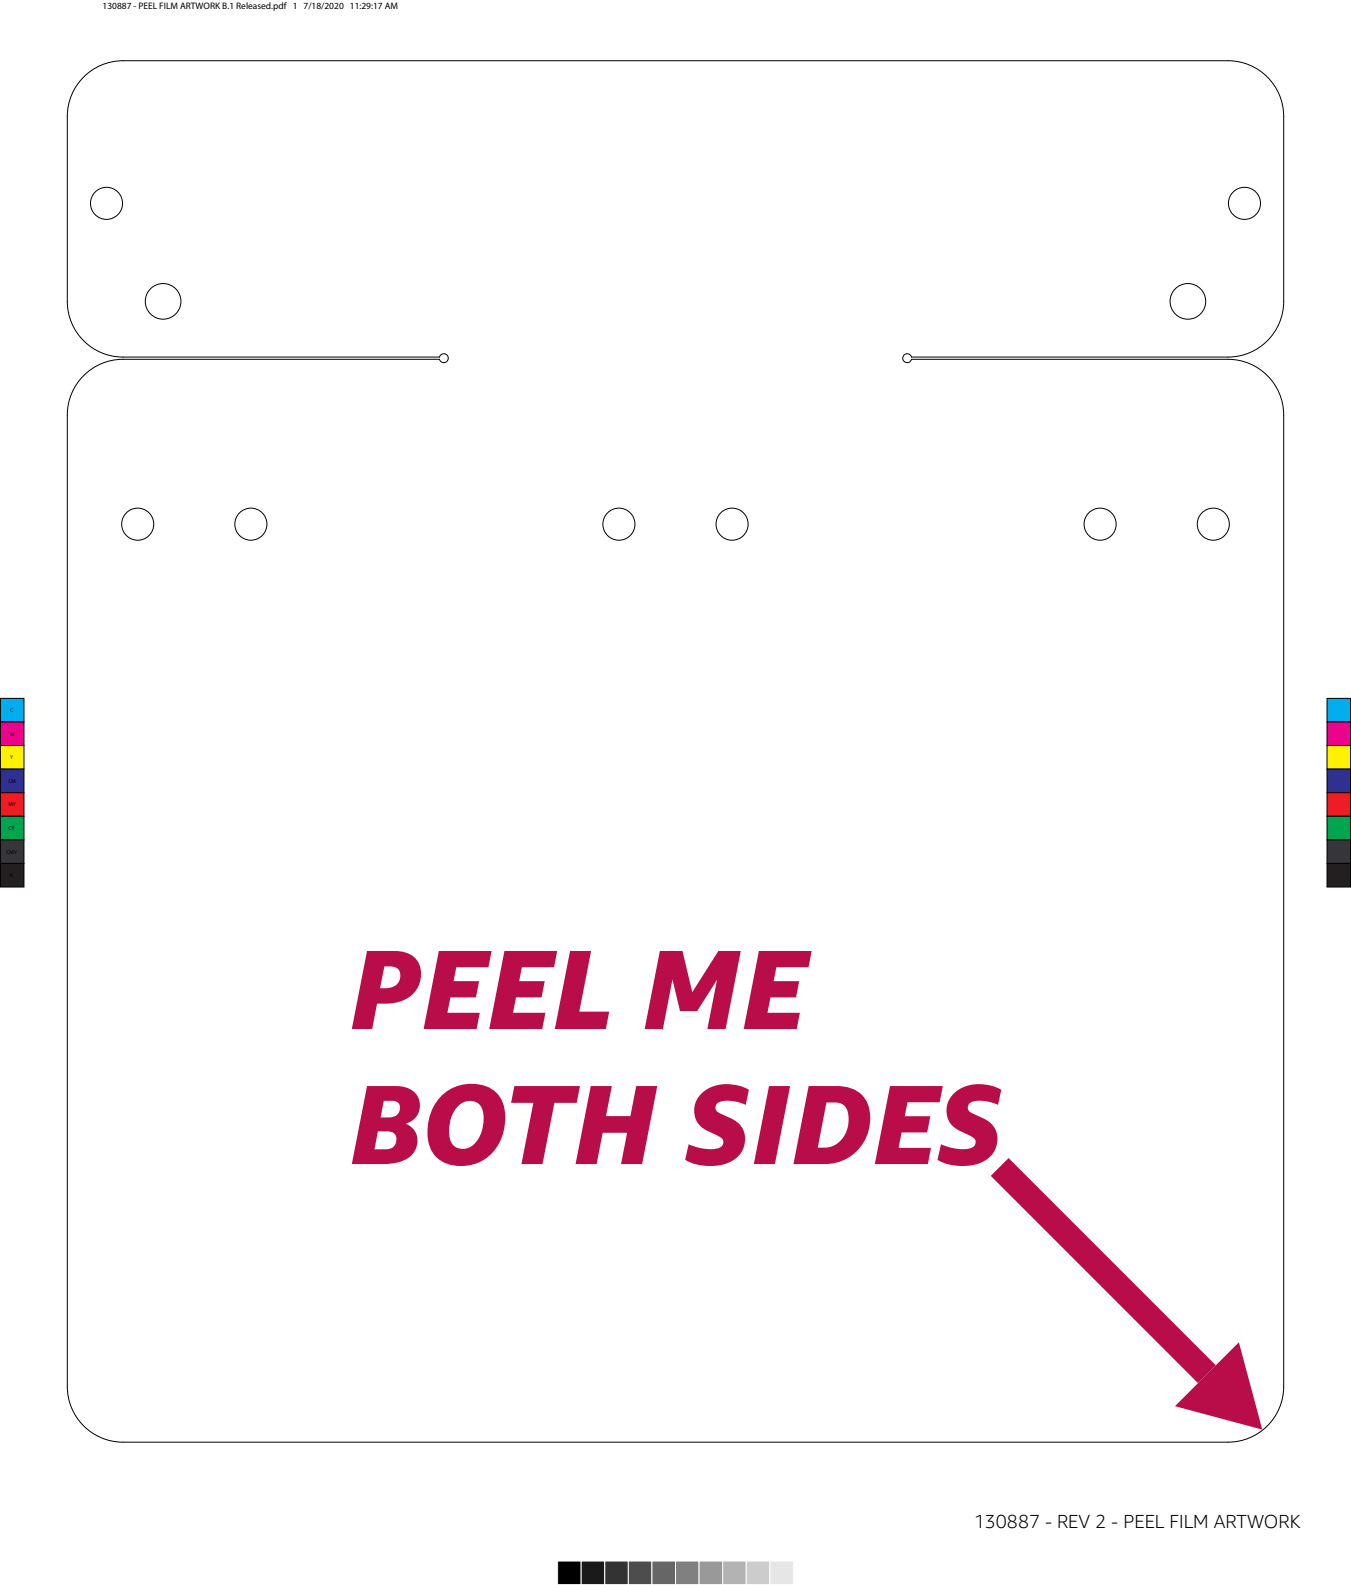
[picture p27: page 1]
PEEL ME BOTH SIDES; CMY

130887 - PEEL FILM ARTWORK B.1 Released.pdf 1 7/18/2020 11:29:17 AM

130887 - REV 2 - PEEL FILM ARTWORK

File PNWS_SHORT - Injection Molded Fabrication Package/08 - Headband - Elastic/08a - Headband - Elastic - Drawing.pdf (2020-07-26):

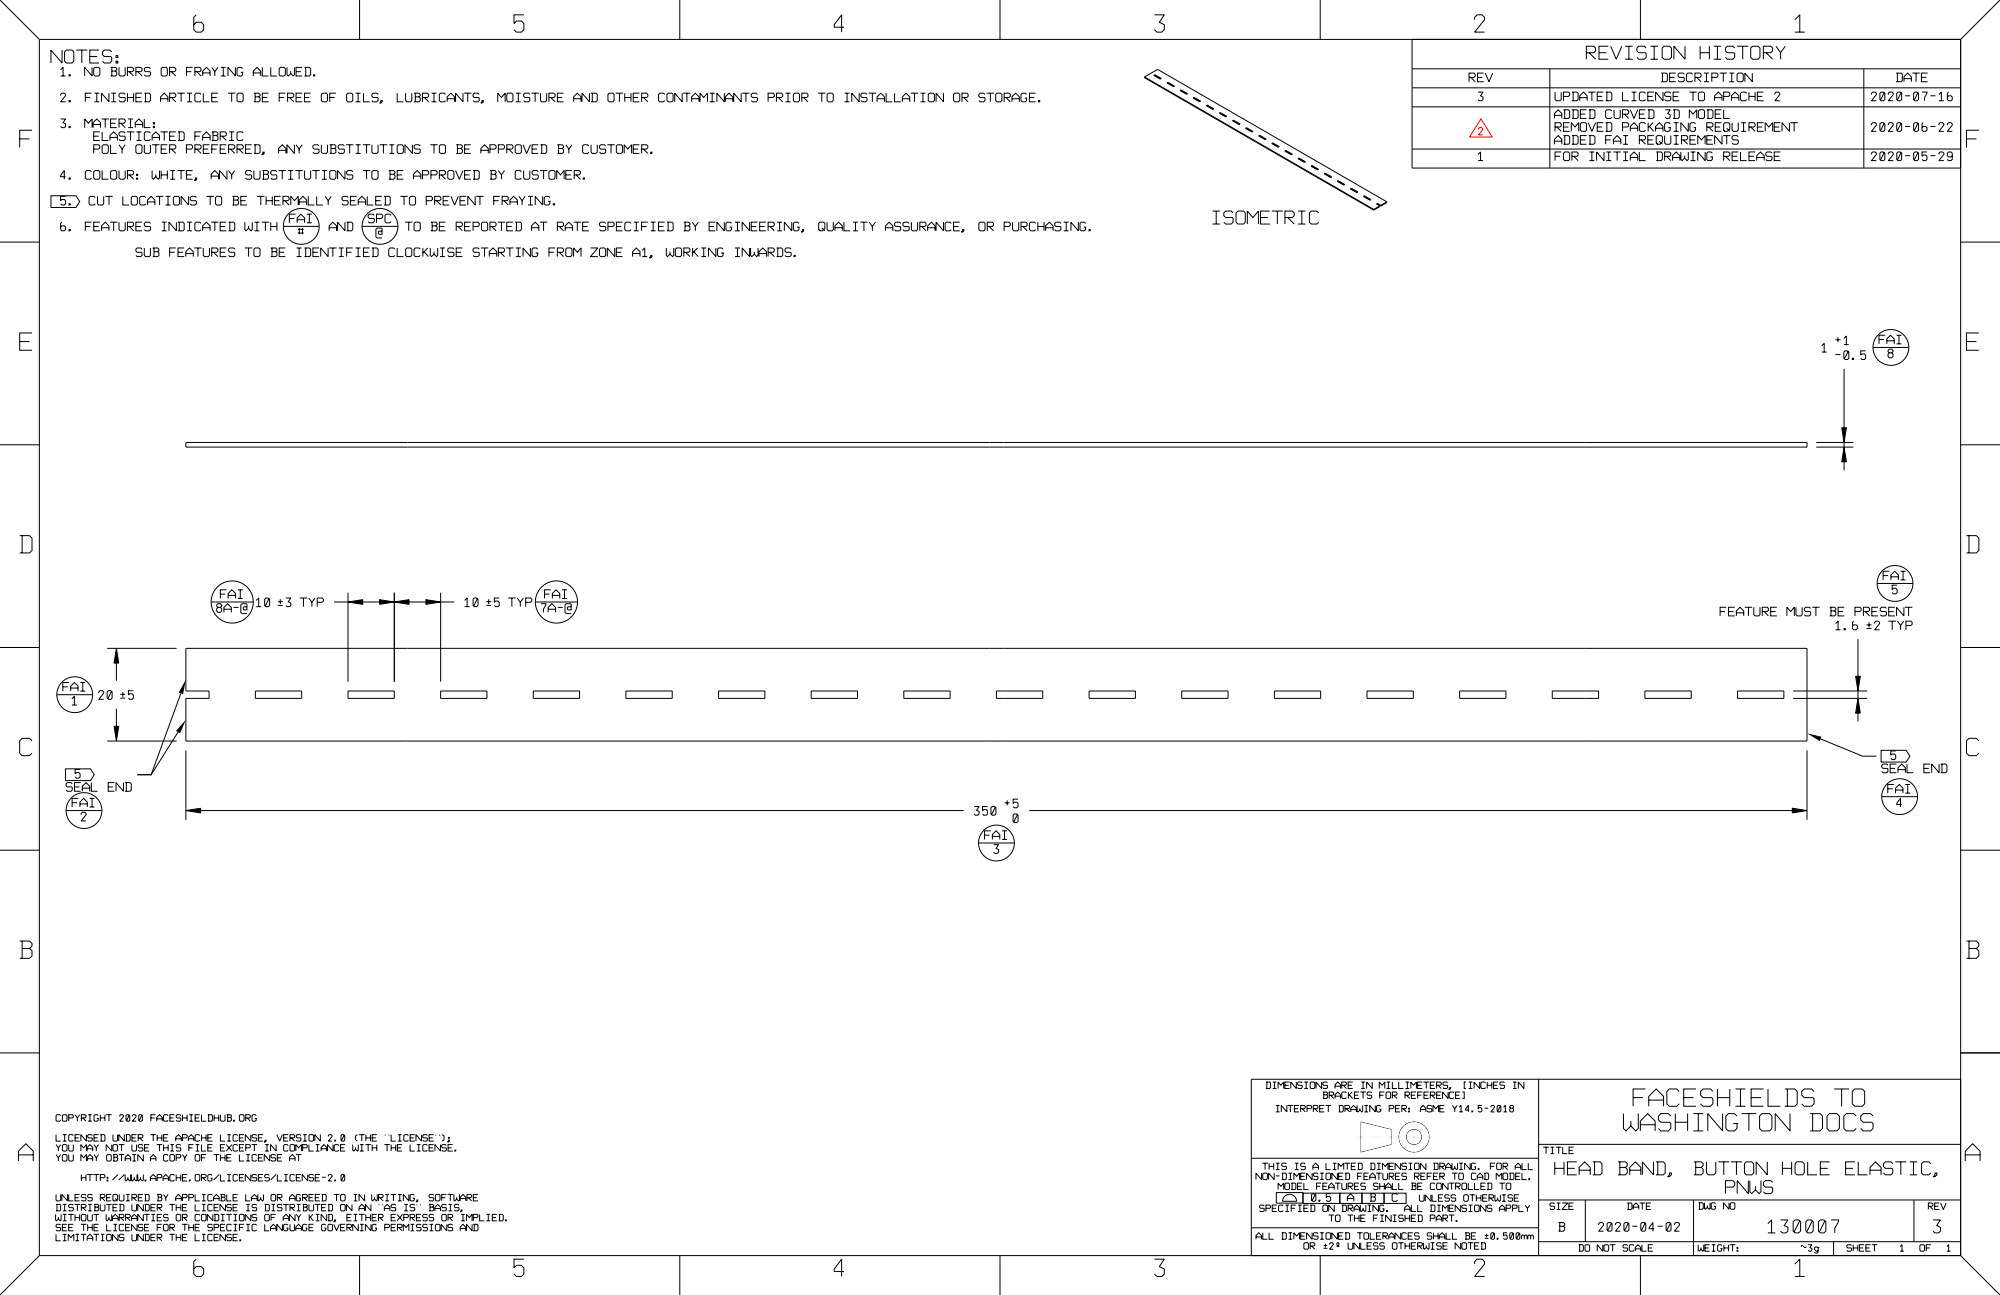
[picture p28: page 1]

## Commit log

2020-04-04 Initial file Commit
    [128827-01 BillOfMaterials.csv, 128828-01 FACESHIELD FRAME PNWS A.1 Released.igs, 128828-01 FACESHIELD FRAME PNWS A.1 Released.stp, 128829-01 - DXF drw00017582 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]
2020-04-04 Renamed files and Folders
    [128828-01 FACESHIELD FRAME PNWS A.1 Released.igs, 128828-01 FACESHIELD FRAME PNWS A.1 Released.stp, 128829-01 - DXF drw00017582 A.1 Released.dxf, 128829-01 FAC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]
2020-04-06 Reaaranging and adding R2
    Adding R2 Fabrication Package
    [128827-01 BillOfMaterials.csv, 128827-02 ASSY FACESHIELD PNWS B.1 Released.stp, 128827-02 BillOfMaterials.csv, 128828-01 FACESHIELD FRAME PNWS A.1 Released.igs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]
2020-04-08 Added i3 MK3S
    Added files for i3 MK3S 0.6 nozzle
    [PNWS B.1 Released_0.6nozzle_0.4mm_PETG_MK3S_1h55m.3mf, PNWS SHORT B.1 Released_0.6nozzle_0.4mm_PETG_MK3S_52m.3mf]
2020-04-08 Updated Face shield files
    [SHIELD GO GAUGE.stl]
2020-04-08 Create PNWS Assembly Instructions.pdf
2020-04-16 New Release Packages
    [05 - BillOfMaterials.csv, 06b - Frame - Full - STL.stl, 06b - Frame - Short - STL.stl, 06c - Frame - Full - STP.stp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]
2020-04-20 Added detail to Readme on print settings
2020-07-26 Adding files for mass production package
    Includes DFM changes for Mass production
    [05 - BillOfMaterials.csv, 06b - Frame - Short - Injection Molding - STEP.stp, 07c - Shield - Origami - DXF.dxf, 07e - Shield - Origami - 3D STEP.stp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]
